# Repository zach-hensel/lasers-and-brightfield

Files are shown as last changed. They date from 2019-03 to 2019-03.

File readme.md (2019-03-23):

# Description

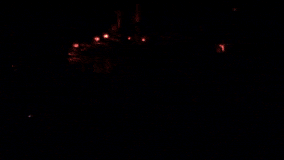
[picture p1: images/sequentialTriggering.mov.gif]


This describes a small hack of the [Micromanager Arduino Sketch](https://valelab4.ucsf.edu/svn/micromanager2/trunk/DeviceAdapters/Arduino/), which can trigger 5 lasers (Oxxius LaserBoxx LBX and LBC models) and 1 neopixel LED ring (rather than 6 lasers). The motivation for doing this was a low-effort way to add brightfield illumination to a microscope setup that already had 5  lasers triggered using the Arduino device adapter in micromanager without learning how to modify device adapters.

This has been tested with micromanager 2.0beta and 2.0gamma with the default arduino device adapter.

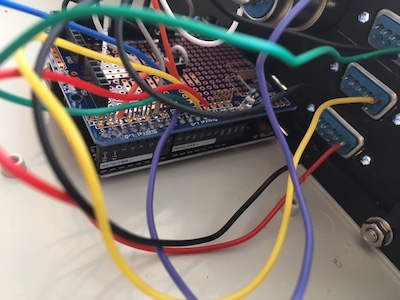
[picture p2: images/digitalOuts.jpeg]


This was inspired by seeing a similar setup in the [Oxford Nanoimager](https://www.youtube.com/watch?v=QzGPyz0SOf8), which looks to have 6 LEDs in a circle with a circumference similar to the Neopixel 12 ring placed a few cm above the sample. With a phase objective, it is possible to achieve [condenser free phase contrast](https://www.ncbi.nlm.nih.gov/pmc/articles/PMC4277858/) using an LED ring, as well as other contrast methods.

All 3d printed components were fabricated by [MiniLab3d](https://minilab3d.pt) via 3dhubs and STL files are in 1-mm units.

## Software

* The Arduino sketch was modified so that commands to trigger the 6th laser instead turn on each pixel in an Adafruit neopixel LED ring. The LED brightness is hardcoded into the Arduino sketch in a #define command; a future update will use the "Set Analogue output" command to instead set the LED intensity since this implementation is not using the analogue output (DAC) device.

* "AOTFcontroller_NP_color.ino" adds the ability to change the color of the Neopixel LEDs and uses some more compact code for assigning LED colors. This is the version that is still under development. DAC channel 2 is used to change LED color (right now, by setting Max Volts to 5 and setting output voltage to 0, 1, 2 or 3 for white, red, green or blue). Up to 4095 colors could be added easily; 24-bit color is technically possible but would be confusing to accomplish with the current Arduino device adapter.

### Installation

1. Modify parameters in #define statements in the Arduino sketch including:
	* `#define BF 20 // default LED intensity (8-bit 0—255)`
	* `#define PN 12 // number of pixels in the LED ring`
	* `#define LS 1 // runs a lightshow whenever pinged for the controller version; set 0 to turn off`
	* `#define PIN 6 // digital out pint to communicate with neopixel ring`
		
2. Wire an Arduino uno to (see below for our specific implementation):
	* Output to trigger TTL devices on pins 8, 9, 10, 11, 12
	* Input on pin 2
	* Output data to Neopixel ring on pin 6
	
3. Compile and upload sketch to Arduino.

4. Install Arduino device adapter including Switch and DAC components; the Neopixel ring will give a short light show if it is configured correctly.

5. Configure settings according to the instructions for the [Arduino device adapter](https://micro-manager.org/wiki/Arduino) with these modifications:
	* A digital output pattern with Pin 13 on will turn on the Neopixel ring (rather than triggering a 6th TTL device)
	* DAC-Volts can be adjusted from 0 (minimum neopixel LED intensity) to 5 (maximum  intensity)
	* Note: If the Neopixel ring is not turning on, the line "tempPattern = tempPattern & B00011111;" can be commented out in the Arduino sketch to diagnose if this is a problem with configuration or connecting the Neopixel ring, because the Arduino Uno has an LED indicating Pin 13 digital out.

## Control box hardware

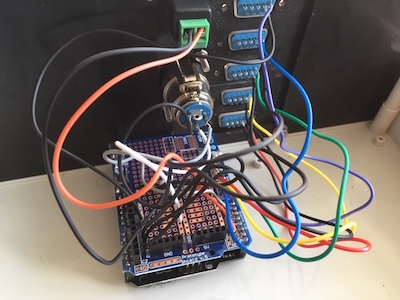
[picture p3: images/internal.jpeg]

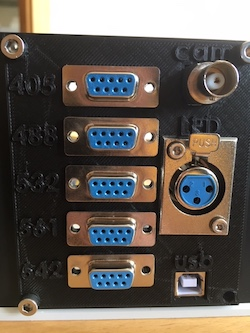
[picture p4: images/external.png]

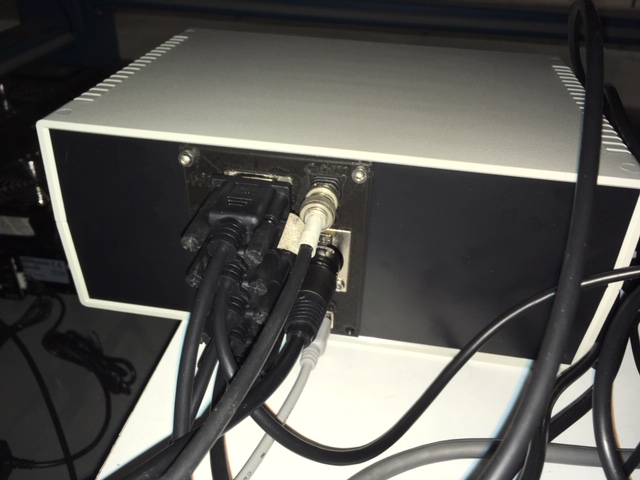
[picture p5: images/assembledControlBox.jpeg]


* Arduino Uno Rev3 powered by USB (From Elegoo starter kit)
* Arduino Proto Shield V5 with some headers removed (from Elegoo starter kit; plastic headers removed with pliers and then pins removed by desoldering)
* 5x female db9 connectors
	* Arduino outputs 8--12 wired to pin 5 (Laser Enable)
	* Arduino ground wired to pin 9 (Digital Ground)
	* Connected to Oxxius lasers using straight-through male-female db9 cable
* 1x female XLR connector (sourced from PT Robotics #PTR002086)
	* Connected to Neopixel LED ring using male-female XLR cable
	* Pin 1 to Arduino ground
	* Pin 2 to Arduino digital output 6
	* Pin 3 to Arduino +5 V
* 1x female BNC connector (sourced from PT Robotics #PTR002965)
	* Connected to triggering device (e.g. camera trigger out); +5 input tested to work with +3.3 V trigger outputs from EMCCD (Photometrics Evolve 512) and sCMOS (Photometrics Prime 95b), but may want to [convert to +5 V](https://github.com/PRNicovich/NicoLase/tree/master/Hardware).
	* Shield to Arduino ground
	* Conductor to Arduino digital input pin 2
	* In our implementation a push-button can also trigger Pin 2 from the +5 Arduino and a 10 kOhm pull-down resistor is also added
* ABS Enclosure cut with rotary tool to fit back panel (sourced from PT Robotics #PTR000810)
* Back panel printed 0.1-mm layers in PLA.
	
## LED ring hardware

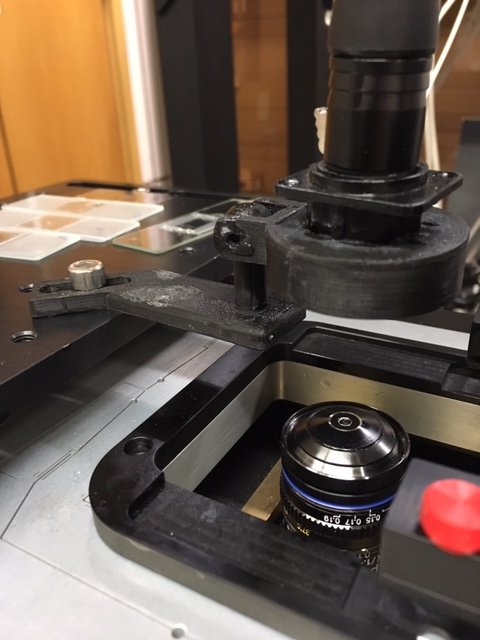
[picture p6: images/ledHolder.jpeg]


* 3d printed neopixel ring holder. Both were printed 0.1-mm layer PLA; in retrospect the LED holder would've been better to print ABS because it warps after fitting to the ball mount. STL files sourced from:
	* Base (can be attached to optical breadboard with M6 screws)
		* MK3_Camera_Ball_Mount.stl from user briankb at thingiverse
		* https://www.thingiverse.com/thing:2828182
		* Licensed CC-BY
	* Light ring
		* picamneopixel holder.stl from user nixternal at thingiverse
		* https://www.thingiverse.com/thing:2189609
		* Modified with rotary tool to add a hole for XLR connector, which was superglued in place
		* Licensed CC-BY-NC-SA
		
* Male XLR connector (sourced from PT Robotics #PTR002090) 
	* Drill hole to accomodate XLR connector within LED ring
	* Super glue in place

* Adafruit Neopixel Ring w/ 12x WS2812 RGB LEDs (sourced PT Robotics #PTR003298)
	* XLR connector Pin 1 to GND
	* XLR connector Pin 2 to IN
	* XLR connector Pin 3 to PWR

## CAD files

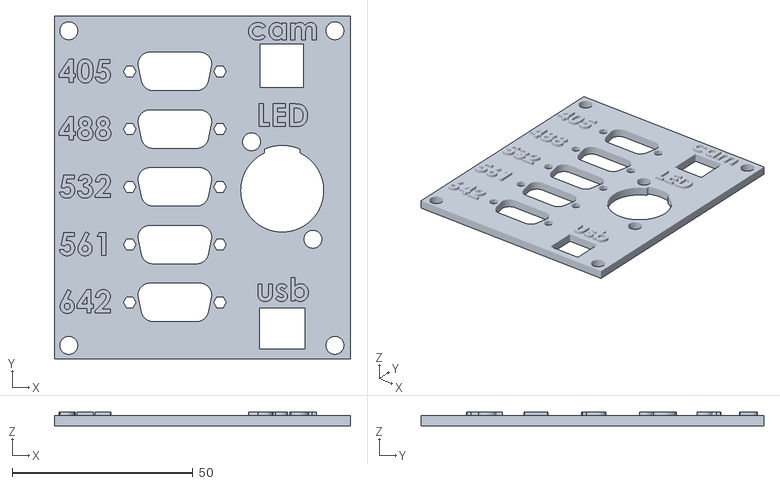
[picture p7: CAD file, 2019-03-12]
back panel/back panel.stl
82.1 x 95.0 x 4.00

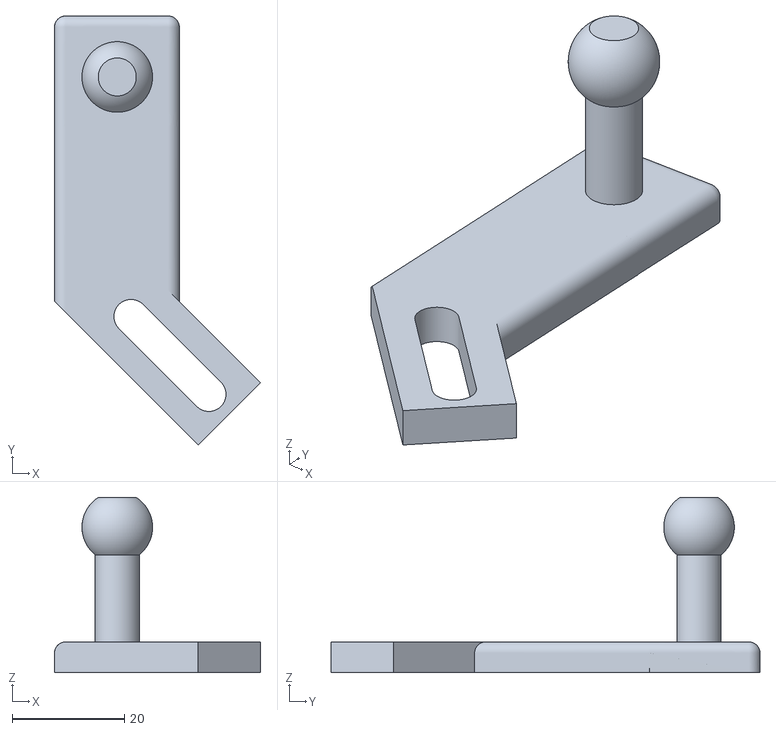
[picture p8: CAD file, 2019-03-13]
led holder/MK3_Camera_Ball_Mount.stl
36.8 x 76.5 x 31.2

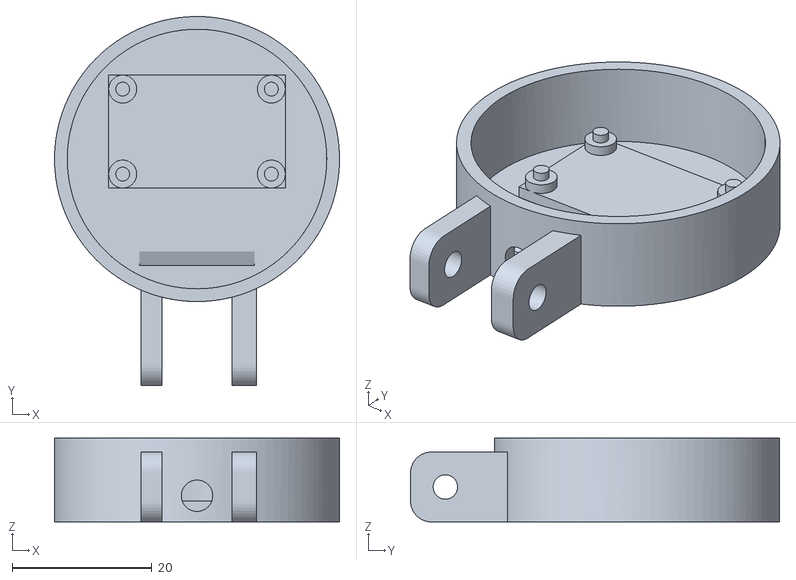
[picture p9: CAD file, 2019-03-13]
led holder/picamneopixel holder.stl
40.7 x 52.7 x 12.0

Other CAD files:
back panel/back panel.dxf

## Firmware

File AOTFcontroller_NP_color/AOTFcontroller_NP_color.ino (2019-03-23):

/* 

Zach Hensel
23 March 2019

This is a modification of the Arduino sketch provided with the Micro-mangager Arduino device adapter; 
it outputs 5 TTL signals to pins 8, 9, 10, 11, and 12, but not to pin 13. Instead, commands from
the micro-manager device adapter that would trigger pin 13 turn on a Neopixel LED strip/ring. Also,
the brightness and color of the Neopixel LEDs can be modified by installing the Arduino DAC peripherals.

Installing in micromanager:

1. Install Arduino device adapter with peripherals Shutter, Switch, DAC1, DAC2
2. DAC1 = LED brightness setting; the "max volts" setting can be anything.
3. DAC2 = LED color; the "max volts" setting MUST stay at the default of 5 for this code to work, and 
    color settings 0, 1, 2, 3 are defined below (White, Red, Green, Blue); the code could be modified
    to have up to 4095 different colors.

Usage: Identical to what's described for the Arduino device adapter: https://micro-manager.org/wiki/Arduino
    with the exception of the two DAC channels

We use this to trigger 5 oxxius lasers (fluorescence) and a Neopixel 12 ring (brightfield; maybe could
    be used for fluorescence.

See our lab's implementation of this here - https://github.com/zach-hensel/lasers-and-brightfield

*/

/*
 * This goal of the application is to set the digital output on pins 8-12 
 * This can be accomplished in three ways.  First, a serial command can directly set
 * the digital output pattern.  Second, a series of patterns can be stored in the 
 * Arduino and TTLs coming in on pin 2 will then trigger to the consecutive pattern (trigger mode).
 * Third, intervals between consecutive patterns can be specified and paterns will be 
 * generated at these specified time points (timed trigger mode).
 *
 * Interface specifications:
 * digital pattern specification: single byte, bit 0 corresponds to pin 8, 
 *   bit 1 to pin 9, etc..  Bits 7 and 8 will not be used (and should stay 0).
 *   ZH190317 -- modified code so that bit 6 sets a neopixel ring rather than laser trigger
 *
 * Set digital output command: 1p
 *   Where p is the desired digital pattern.  Controller will return 1 to 
 *   indicate succesfull execution.
 *
 * Get digital output command: 2
 *   Controller will return 2p.  Where p is the current digital output pattern
 *
 * Set Analogue output command: 3xvv
 *   Where x is the output channel (either 1 or 2), and vv is the output in a 
 *   12-bit significant number.
 *   Controller will return 3xvv:
 *   ZH190317 -- hijacked this command to instead change LED intensity (channel 1) and color (channel 2)
 *
 * Get Analogue output:  4
 *
 *
 * Set digital patten for triggered mode: 5xd 
 *   Where x is the number of the pattern (currently, 12 patterns can be stored).
 *   and d is the digital pattern to be stored at that position.  Note that x should
 *   be the real number (i.e., not  ASCI encoded)
 *   Controller will return 5xd 
 *
 * Set the Number of digital patterns to be used: 6x
 *   Where x indicates how many digital patterns will be used (currently, up to 12
 *   patterns maximum).  In triggered mode, after reaching this many triggers, 
 *   the controller will re-start the sequence with the first pattern.
 *   Controller will return 6x
 *
 * Skip trigger: 7x
 *   Where x indicates how many digital change events on the trigger input pin
 *   will be ignored.
 *   Controller will respond with 7x
 *
 * Start trigger mode: 8
 *   Controller will return 8 to indicate start of triggered mode
 *   Stop triggered a 9. Trigger mode will  supersede (but not stop) 
 *   blanking mode (if it was active)
 * 
 * Stop Trigger mode: 9
 *   Controller will return 9x where x is the number of triggers received during the last
 *   trigger mode run
 *
 * Set time interval for timed trigger mode: 10xtt
 *   Where x is the number of the interval (currently, 12 intervals can be stored)
 *   and tt is the interval (in ms) in Arduino unsigned int format.  
 *   Controller will return 10x
 *
 * Sets how often the timed pattern will be repeated: 11x
 *   This value will be used in timed-trigger mode and sets how often the output
 *   pattern will be repeated. 
 *   Controller will return 11x
 *  
 * Starts timed trigger mode: 12
 *   In timed trigger mode, digital patterns as set with function 5 will appear on the 
 *   output pins with intervals (in ms) as set with function 10.  After the number of 
 *   patterns set with function 6, the pattern will be repeated for the number of times
 *   set with function 11.  Any input character (which will be processed) will stop 
 *   the pattern generation.
 *   Controller will retun 12.
 * 
 * Start blanking Mode: 20
 *   In blanking mode, zeroes will be written on the output pins when the trigger pin
 *   is low, when the trigger pin is high, the pattern set with command #1 will be 
 *   applied to the output pins. 
 *   Controller will return 20
 *
 * Stop blanking Mode: 21
 *   Stops blanking mode.  Controller returns 21
 *
 * Blanking mode trigger direction: 22x
 *   Sets whether to blank on trigger high or trigger low.  x=0: blank on trigger high,
 *   x=1: blank on trigger low.  x=0 is the default
 *   Controller returns 22
 * 
 * Get Identification: 30
 *   Returns (asci!) MM-Ard\r\n
 *
 * Get Version: 31
 *   Returns: version number (as ASCI string) \r\n
 *
 * Read digital state of analogue input pins 0-5: 40
 *   Returns raw value of PINC (two high bits are not used)
 *
 * Read analogue state of pint pins 0-5: 41x
 *   x=0-5.  Returns analogue value as a 10-bit number (0-1023)
 *
 *
 * 
 * Possible extensions:
 *   Set and Get Mode (low, change, rising, falling) for trigger mode
 *   Get digital patterm
 *   Get Number of digital patterns
 */

#include <Adafruit_NeoPixel.h>
#define PIN 6 // neopixel drive pin
#define NP 12 // number of neopixels to use
#define BF 32 // initial brightfield level for neopixels (0-255)
#define LS 1 // whether or not lightshow should play when Arduino initialized (when it is pinged for its version)

// Initialize Neopixel ring

Adafruit_NeoPixel strip = Adafruit_NeoPixel(NP, PIN, NEO_GRB + NEO_KHZ800); // have to change this line for different types of LEDs

unsigned int LEDintensity_ = BF; // set initial LED intensity
uint32_t LEDcolor_ = strip.Color(LEDintensity_,LEDintensity_,LEDintensity_);

uint32_t black_ = strip.Color(0,0,0); // define black for turning off LEDs

bool NPon_ = false; // variable to track if neopixel array is on or off

// Unmodified code from mm arduino sketch starting here; only modified to call "modPORTB" rather than setting PORTB directly
 
unsigned int version_ = 2;

// pin on which to receive the trigger (2 and 3 can be used with interrupts, although this code does not use interrupts)
int inPin_ = 2;
// to read out the state of inPin_ faster, use 
int inPinBit_ = 1 << inPin_;  // bit mask 

// pin connected to DIN of TLV5618
int dataPin = 3;
// pin connected to SCLK of TLV5618
int clockPin = 4;
// pin connected to CS of TLV5618
int latchPin = 5;

const int SEQUENCELENGTH = 12;  // this should be good enough for everybody;)
byte triggerPattern_[SEQUENCELENGTH] = {0,0,0,0,0,0,0,0,0,0,0,0};
unsigned int triggerDelay_[SEQUENCELENGTH] = {0,0,0,0,0,0,0,0,0,0,0,0};
int patternLength_ = 0;
byte repeatPattern_ = 0;
volatile long triggerNr_; // total # of triggers in this run (0-based)
volatile long sequenceNr_; // # of trigger in sequence (0-based)
int skipTriggers_ = 0;  // # of triggers to skip before starting to generate patterns
byte currentPattern_ = 0;
const unsigned long timeOut_ = 1000; // ZH made timeout longer for testing with serial monitor
bool blanking_ = false;
bool blankOnHigh_ = false;
bool triggerMode_ = false;
boolean triggerState_ = false;
 
void setup() {
   // Higher speeds do not appear to be reliable
   Serial.begin(57600);
  
   pinMode(inPin_, INPUT);
   pinMode (dataPin, OUTPUT);
   pinMode (clockPin, OUTPUT);
   pinMode (latchPin, OUTPUT);
   pinMode(8, OUTPUT);
   pinMode(9, OUTPUT);
   pinMode(10, OUTPUT);
   pinMode(11, OUTPUT);
   pinMode(12, OUTPUT);
   pinMode(13, OUTPUT);
   
   // Set analogue pins as input:
   DDRC = DDRC & B11000000;
   // Turn on build-in pull-up resistors
   PORTC = PORTC | B00111111;
   
   digitalWrite(latchPin, HIGH);
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

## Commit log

2019-03-12 initial stuff
    [back panel.dxf, back panel.stl]
2019-03-17 modified arduino sketch; must test
2019-03-18 updated readme, arduino sketch after testing with micromanager and lasers, and added some pictures
2019-03-19 fix a bug and reduce timeout to match arduino distribution in micromanager
2019-03-23 New version that can also modify LED color
